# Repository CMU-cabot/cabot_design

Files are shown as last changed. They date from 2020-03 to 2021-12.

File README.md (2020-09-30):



# CaBot

CaBot (Carry on Robot) is an AI suitcase to help people with visually impairments travel independently. Can you imagine to walk around at airports without vision? It’s huge open space and there are lots of things and people, so that it is really dangerous for them to walk around at airports.

With CaBot, people with visually impairments will be able to enjoy their travel time more freely, and they will be free from asking someone to help.

## Design Documents

|Type|Description|
|---|---|
|CaBot1|Initial prototype of CaBot, tactile handle, geared motor + electric clutch [[1]](#1)|
|[CaBot2-e2](./cabot2-e2/)|Second prototype of CaBot2-e, tactile handle, direct drive|
|[CaBot2-gt](./cabot2-gt/)|Prototype based on a commercial suitcase, tactile handle, direct drive|

<a name="1">[1]</a> [ASSETS 2019 paper: CaBot: Designing and Evaluating an Autonomous Navigation Robot for Blind People](https://dl.acm.org/doi/10.1145/3308561.3353771)

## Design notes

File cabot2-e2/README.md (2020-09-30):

# CaBot2-e2

This repository provides three dimensional files for CaBot2-e2 parts and an instruction to build the robot from scratch.
CaBot2-e2 has an aluminum chassis mounting two direct drive brushless DC motors, two casters, and covered by a suitcase. 
The handle has tactile vibrators and input buttons for user interface. 

<p align="center">
  
</p>

## Parts list

The list of components needed for assembling a Cabot are enlisted in [this page](./parts.md)

## Assembly Schematic

The following diagram provides an overview of the assembled view of Cabot and [cabot-e-arduino](https://github.com/CMU-cabot/cabot-e-arduino.git) repository has the wiring diagram and the code relevant to the handle (push buttons, touch sensor and vibrators) interface with Arduino Mega 2560.

<p align="center">
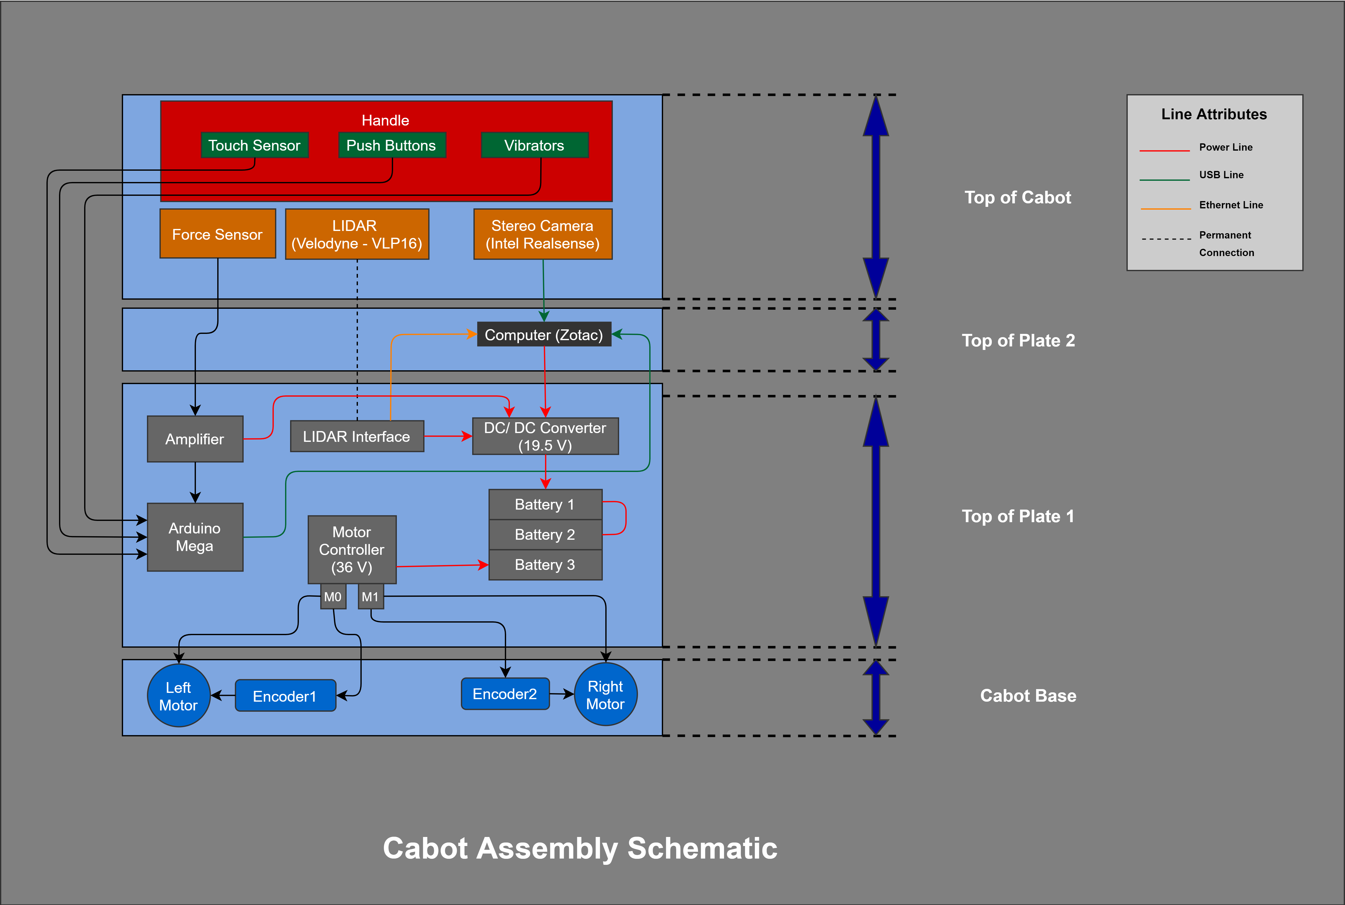
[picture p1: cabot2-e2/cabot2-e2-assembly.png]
  
</p>

## Assembly instructions

<p align="center">
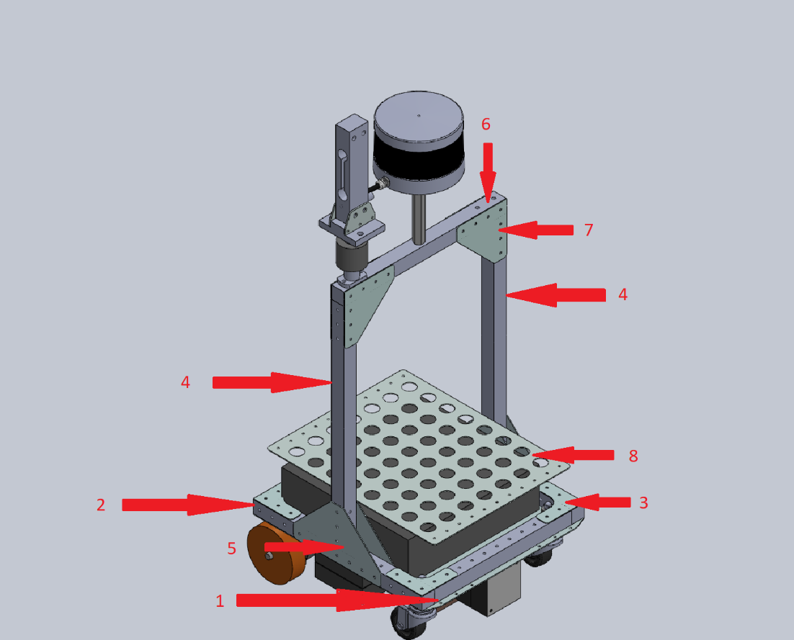
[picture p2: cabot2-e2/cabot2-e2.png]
  
</p>

1. First procure the base plate of the robot along with all the required electronic components that need to be assembled on the robot.
2. Next, attach the drive motor clamp and the two caster wheels to the base plate (1).
3. Next, decide what components should be attached to the base plate (1) and then assemble the components on the plate. For example: If you need the Arduino Mega, Motor Controller, batteries and some other components on the top of base plate, then mount these components on the plate with the help of mounting screws that pass through several of the provided holes.
4. Next attach the four medium length tubes (2) to the four corners of the base plate (1) as shown in figure. It is preferable to clamp them to the base plate (1) with the help of several rivets using a rivet tool.
5. Then, attach the four L-shaped clamps (3) to the four corners of tubes (2) as shown in figure and clamp them with the help of rivets.
6. Later, attach the vertical chassis members (4) of the robot to the robot side body facing the wheels. The members (4) must be attached to the midpoint of tubes (2) using the triangular clamps (5) as shown in figure. It is advised to use several rivets to clamp them permanently for a sturdier fit.
7. Next, attach the top chassis member (6) using triangular clamps and suitable number of rivets. Please note that the triangular clamps should be attached on both sides of the connection.
8. Later, attach the force sensor to right corner of the chassis member (6) when the robot is front facing. You can use screws for attaching the force sensor.
9. Next the handle should be assembled separately using rivets and then connected to the top portion of the force sensor.

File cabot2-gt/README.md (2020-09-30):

# CaBot2-GT

This CaBot has the same motor drive with CaBot2-e2, but is based on [Globe Trotter](https://www.globe-trotter.com/)'s carbon fiber suitcase which is designed by [Hideki Yoshimoto](http://www.tangent.uk.com/about/).

<center>
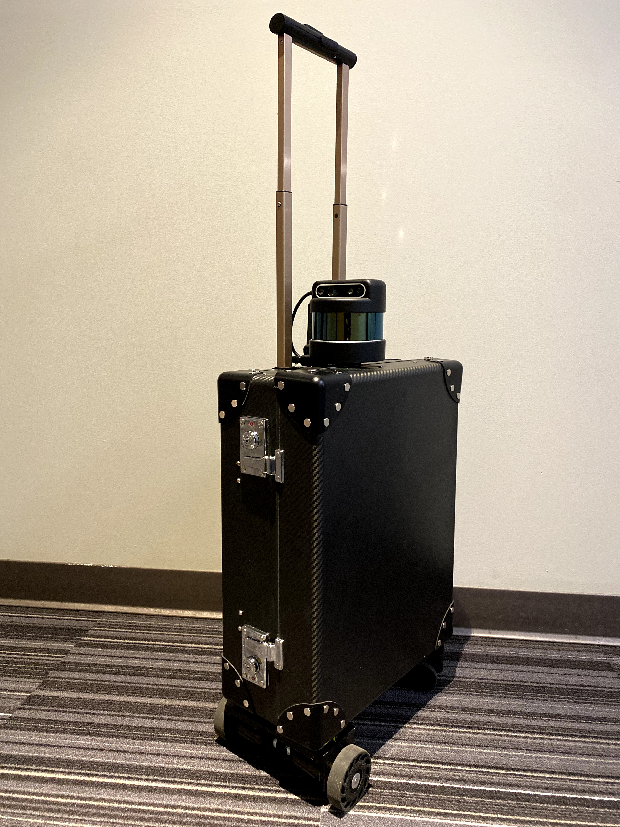
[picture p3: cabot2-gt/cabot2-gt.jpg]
  
  &nbsp;&nbsp;&nbsp;&nbsp;
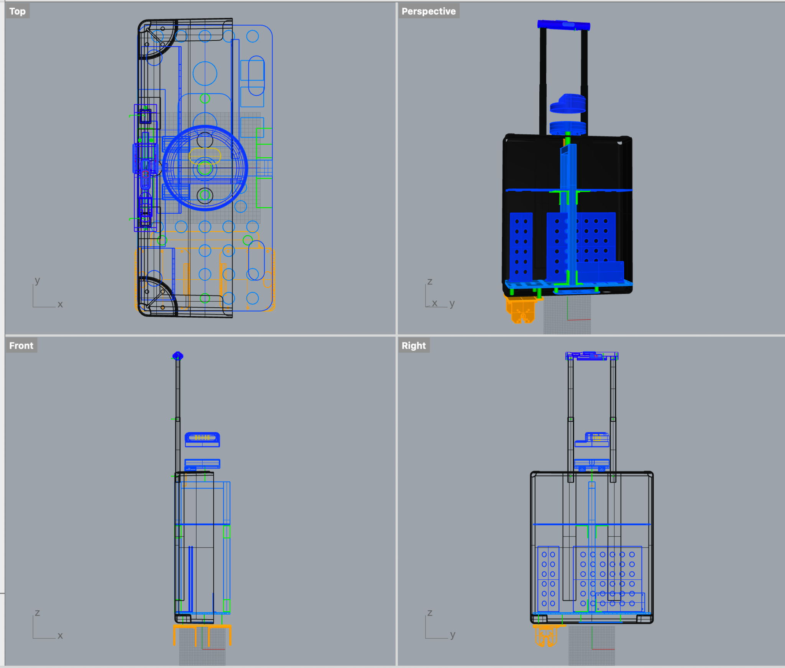
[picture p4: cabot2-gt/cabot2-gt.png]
  
</center>

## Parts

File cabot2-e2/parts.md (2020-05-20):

| Category | Item | Quantity | Specification | Description | Example Item |
| --- | --- | --- | --- | --- | --- |
| Body | Aluminum Frame | 1 | see [**cabot2_e2.stp**](https://github.com/CMU-cabot/cabot_design/blob/master-filter/cabot2_e2/cabot2_2e.stp) file |  |  |
| Body | Rivet | 100 | 1/8" x 23/64" |  | [Link](https://www.amazon.com/dp/B0727XS1XC/) |
| Body | Suitcase (Cover) | 1 | Carry-on lagguage fits to CaBot | Delivered through Amazon (CMU version) | [Link](https://www.amazon.com/dp/B0727XS1XC) |
| Body | Screw | 25 | M3, 16mm length, Hex Socket |  |  |
| Body | Screw | 10 | M3, 32mm length, Hex Socket |  |  |
| Body | Washer | 20 | M3 |  |  |
| Body | Lock nut | 20 | M3, 0.5 mm thread, Hex lock Nut |  |  |
| Body | Screw | 8 | M6, 10mm length, Hex Socket (no nuts required) | to fix handle and the force sensor |  |
| Body | Spacer | 4 | Φ3mm, 60mm height, dual female hex pillar |  | [Link](https://www.newegg.com/p/0PS-008N00223?item=9SIA27C3TJ0345) |
| Handle | Handle Print | 1 | see [**stl files under handle directory**](https://github.com/CMU-cabot/cabot_design/tree/master-filter/cabot2_e2/handle) | print one each |  |
| Handle | Tactile push button | 4 | 6x6x4.3mm | handle buttons |  |
| Handle | Prototype PCB | 1 | 2.54mm interval, 6 x 9 holes | attach 4 buttons and insert into the handle |  |
| Handle | Arduino Nano | 1 | Arduino Nano | Can be merge into Arduino Mega, but keep separated configuration |  | 
| Handle | cables/headers | 10 | wire and pin header between handle and nano | wire from handle to Arduino Nano |  |
| Handle | Vibrators | 3 | Dimension: 10mm diameter, 2.7mm thick | attached to handle | [Link](https://www.adafruit.com/product/1201) |
| Handle | Soft double adhesive tape | 1 | 1/8 inch thinkness x 7/8 inch width x 5 inch length total | needs to put this between vibrator and the handle | [Link](https://www.amazon.com/dp/B07GBMT736) |
| Mobility | Motor | 2 | DUAL SHAFT MOTOR - D5065 270KV |  | [Link](https://odriverobotics.com/shop/odrive-custom-motor-d5065) |
| Mobility | Encoder | 2 | CUI AMT102-V |  | [Link](https://odriverobotics.com/shop/cui-amt-102) |
| Mobility | Controller | 1 | 56V, connector is optional | with connector is easy to insatll | [Link](https://odriverobotics.com/shop/odrive-v36) |
| Mobility | Wheel | 2 | 2 7/8 inch ~ 3 inch, black or matched color with the suitcase cover |  | [Link](http://www.banebots.com/product/T81P-294BO.html) |
| Mobility | Wheel Hub | 2 | 8mm shaft |  | [Link](http://www.banebots.com/product/T81H-RM81.html) |
| Mobility | Caster | 2 | 1 5/8 inch wheel, 3/8 16 thread |  | [Link](https://www.mcmaster.com/2834T11) |
| Mobility | Nut | 4 | 3/8 16 thread | two nuts under body (kind of spacer) |  |
| Mobility | Lock nut | 2 | 3/8 16 thread | one lock nut above body |  |
| PC | Zotac | 1 | ZBOX-EN72070V |  | [Link](https://store.zotac.com/magnus-en72070v-with-windows-10-zbox-en72070v-u-w2b) |
| PC | Memory | 2 | DDR4 SODIMM 2666, 16 GB |  |  |
| Power | Power connector | 1 | 7.4 x 5.0 mm connector (Zotac 2070) | Regulator -> PC |  |
| Power | DC/DC Regulator | 1 | 15A (300w @ 19.5v) | 36v -> 19.5v, PC, force sensor, and LiDAR | [Link](https://www.amazon.com/dp/B01GFVI6R6) |
| Power | Cable+connector | 1 | XT60 Female, 14AWG | battery2 (parallel) to regulator |  |
| Power | Battery on off switch | 1 | XT60 Female, 14AWG | between battery1 and motor controller |  |
| Power | 12 Gage cable | 1 | 12AWG | motor controller to motor |  |
| Power | Battery | 3 | 36V 98Wh (less than 100wh) | CaBot requires at least 3 (2 for computer, 1 for motor) | [Link](https://www.ebikes.ca/shop/electric-bicycle-parts/batteries/36v-ligo-battery.html#) |
| Power | Charger | 2 | 36V 2A Charger | 2 chargers are combenient | [Link](https://www.ebikes.ca/shop/electric-bicycle-parts/chargers/36v-2a-charger.html) |
| Sensor | Force Sensor | 1 | 3kg |  | [Link](https://item.taobao.com/item.htm?spm=a1z09.2.0.0.66402e8dYOsXI3&id=534342186657&_u=43jn0h9vc1e9) |
| Sensor | Sensor Amplifier | 1 |  |  | [Link](https://item.taobao.com/item.htm?spm=a1z10.5-c.w4002-4299160466.30.16598d968WM9IO&id=547565359463) |
| Sensor | Arduino mega | 1 | Arduino Mega |  | [Link](https://store.arduino.cc/usa/mega-2560-r3) |
| Sensor | BNO055 adafruit | 1 | BNO055 adafruit, not from other company because they also provides library to ctonrol sensors | IMU (connecting to Arduino Mega) |  |
| Sensor | MPR121 adafruit | 1 | MPR121 adafruit, not from other company because they also provides library to ctonrol sensors | capacitive Touch sensor (connecting to Arduino Mega) |  |
| Sensor | Conductive tape | 1 | Condactive |  |  |
| Sensor | Arduino mega shield | 1 | General shield or Cabot's custom PCB | with pins | [Link](https://github.com/RealCabot/simplePCB) |
| Sensor | RealSense D435 | 1 |  |  |  |
| Sensor | Velodyne | 1 | Velodyne VLP16 (Pack Lite) |  | 
| Sensor | Camera mount pall | 1 | 1/4 inch - 20 thread (female and male), 10cm long | Something like in the url |  |
| Sensor | Screw | 1 | 1/4 inch - 20 thread |  |  |
| Sensor | Flat washer | 2 | 1/4 inch - 1 inch | to protect pipe from vending |  |
| Sensor | Lock Nut | 1 | 1/4 inch - 20 thread | to shorten the male threads (put it between pole and lidar) |  |
| Misc | Ethercable | 1 | RJ45, 1 feet |  |  |
| Misc | HDMI dumy | 1 |  |  | [Link](https://www.amazon.com/dp/B07FB64V4Y) |
| Misc | USB hub | 1 | USB2.0 | to prevent wireless signal interference from USB3.0 |  |
| Misc | Speaker | 1 | Small, USB power, Line-in | Optional | [Link](https://www.amazon.com/dp/B07QDPRYYD) |

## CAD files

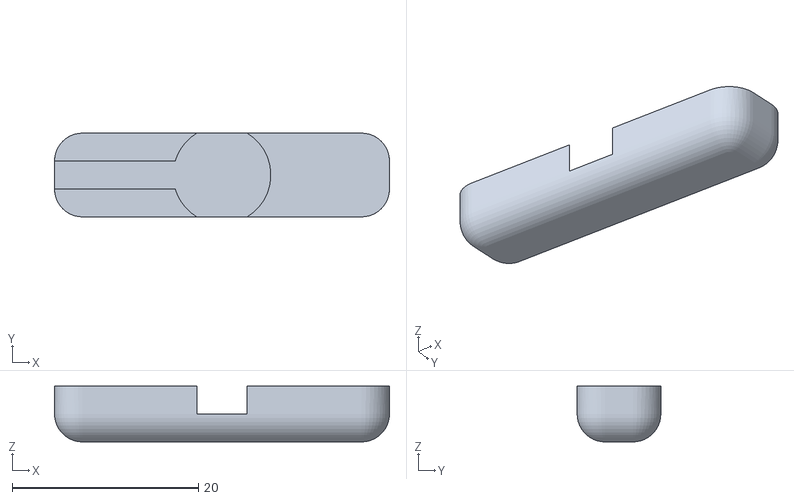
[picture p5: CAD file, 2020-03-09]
cabot2-e2/handle/right_vibrator.STL
36.0 x 9.00 x 6.00

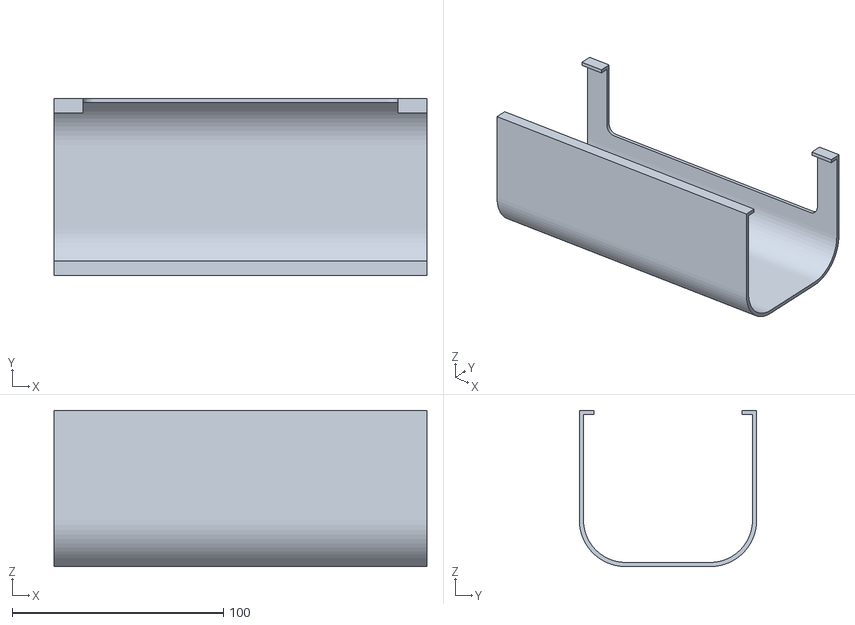
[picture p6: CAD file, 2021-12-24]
cabot2-gt/GT_motor_cover.stl
176.6 x 84.0 x 74.0

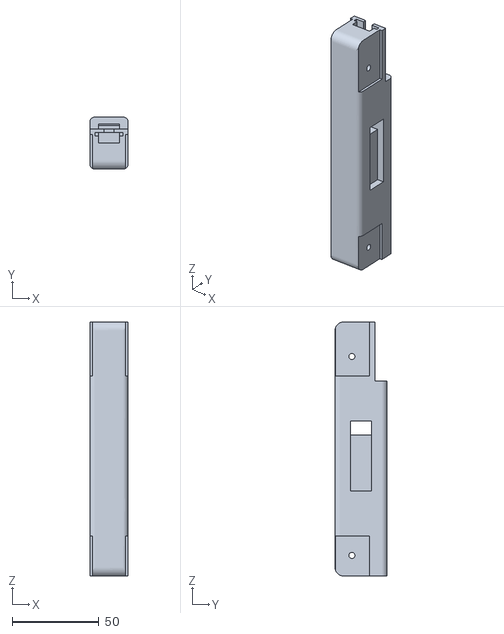
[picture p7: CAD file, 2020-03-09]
cabot2-e2/handle/handle_body.STL
22.0 x 30.0 x 146.0

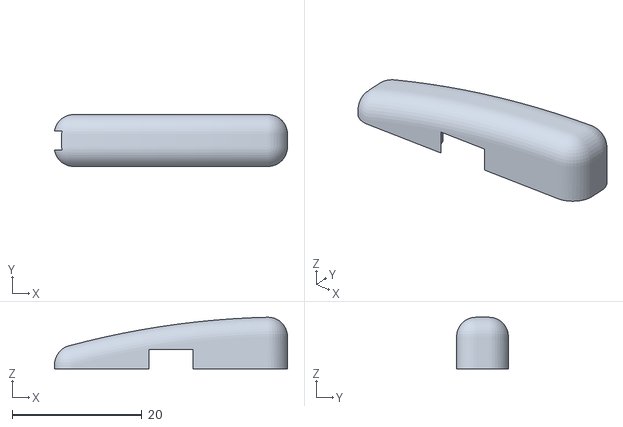
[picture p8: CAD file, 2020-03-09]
cabot2-e2/handle/top_vibrator.STL
36.0 x 8.00 x 7.96

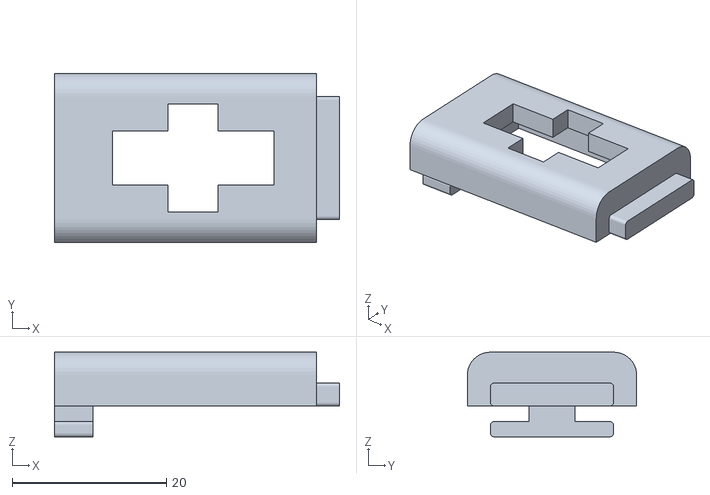
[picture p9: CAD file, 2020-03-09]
cabot2-e2/handle/buttons_cover.STL
37.0 x 22.0 x 11.0

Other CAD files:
cabot2-gt/GT_motor_cover.f3d
cabot2-gt/GT_motor_cover.ipt

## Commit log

2020-05-18 Added cabot assembly figures
2020-09-30 organize contents and add CaBot2-GT design
    [buttons_cover.STL, handle_body.STL, left_vibrator.STL, right_vibrator.STL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]
2021-12-24 Add files via upload
    add motor cover models
    [GT_motor_cover.f3d, GT_motor_cover.ipt, GT_motor_cover.stl]

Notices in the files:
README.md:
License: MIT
